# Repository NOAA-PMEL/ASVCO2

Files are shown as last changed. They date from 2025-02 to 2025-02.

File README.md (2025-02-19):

# ASVCO2
Open Source Repository for the Autonomous Surface Vehicle CO2 (ASVCO2) gen2 system's firmware and electronics hardware.

## Attribution
You agree to acknowledge NOAA-PMEL and UW on splash pages, and in publications, for products developed with this software.

## UW License
*Refer to the LICENSE file.*

## NOAA Legal Disclaimers
*NOAA does not intend to patent this work worldwide. It may be used freely, but NOAA does not warrant its fitness for any use.*

*As a work of the United States Government, the associated schematics and software are in the public domain within the United States. Additionally, NOAA waives any potential copyright and related rights in the associated schematics and software worldwide.*

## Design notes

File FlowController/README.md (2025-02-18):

# EDD-FlowController
Dedicated Flow Controller module which can control up to eight valves, four small motors, or a combination of both.  Design is originally for MApCO2 refresh project.

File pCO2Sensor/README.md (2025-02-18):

# EDD-pCO2Sensor
Gen2 pCO2 sensor based off of MApCO2 technology, upgraded with MSP430FR and active parts.

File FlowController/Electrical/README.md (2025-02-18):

# EDD-flow-controller-kicad
KiCad port of ASVCO2 Flow Control board

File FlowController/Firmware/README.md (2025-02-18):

# FlowController - Firmware
## Changelog
v1.2 SPON, SPOFF/SPVENT valve setting changed.  

## Build tools
This project uses the following build tools:
| Tool | Version | Description |
|----|----|----|
| IAR Embeddded Workbench for MPS430 | v7.20.1 | Embedded C/C++ Compiler for MSP430|
| Ceedling | 0.28.2 | Automated testing framework for C applications |
| CException | 1.3.1.18 | Simple Exception Handling for C|
| CMock | 2.4.4.215 | Mocking framework used with Ceedling |
| Unity | 2.4.1.120 | Unit test framemwork |

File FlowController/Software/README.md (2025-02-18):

# Flow Controller User Interface
## Overview
This document contains operational information for the Flow Controller Graphic User Interface, Command Line Interface and direct communication with the Flow Controller over RS-232

----------------------------------------------------------------
## Python Installation Instructions
The CLI and the GUI require Python 3.9 or later to be installed, as well as a virtual environment to run in.  
### Creating a virtual environment and installing required packages
1. Install Python 3.9 or later if not already installed
2. Open a terminal (In windows you can use CMD or PowerShell)
3. Navigate to this README directory (path/EDD-FlowController/Software/FlowControllerUI/)
4. run the following commands
    ```cmd
    > python -m venv .venv
    For Windows
    > .venv\Scripts\activate
    for Linux
    > source .venv/bin/activate
    
    > python -m pip install -r requirements.txt
    ```
5. Wait for the packages to be installed and then the GUI and CLI will be ready to run

----------------------------------------------------------------
## Direct Communication with Flow Controller (RS-232)
The Flow Controller uses a simple RS-232 interface to communicate with the host (ASVCO2, user, etc.).  

### RS-232 Settings
* Baudrate: 9600
* Bits: 8
* Flow Contro: None
* Stop Bits: 1

### RS-232 Commands
* All commands are terminated with "\r\n"
* All commands respond with ACK (0x06) if valid or NACK (0x15) if invalid
  * This response will be referred to as *\<A/N\>* in the following table
* All command respond with current 6 valve and 1 pump settings
    *  (ABABAB1 would be V1=ac, V2=bc, V3=ac, V4=bc, V5=ac, V6=bc, Pump=ON))
    *  This Response will be referred to as *\<VALVE\>* in the following table

| Command | Response | Description |
| --- | --- | --- |
| mode | *\<A/N\>* **MODE: XXX**\r\n *\<VALVE\\>* | Get the current mode |
| mode=SSSSS | *\<A/N\>* *\<VALVE\>* | Set the Mode to SSSSSS *See modes below | 
| vac=X | *\<A/N\>* *\<VALVE\>* | Set Valve X to position AC |
| vbc=X | *\<A/N\>* *\<VALVE\>* | Set Valve X to position BC |
| current | *\<A/N\>* **CURRENT: X**\r\n *\<VALVE\>* | Read Current Setting (1 - 7) |
| current=X | *\<A/N\>* *\<VALVE\>* | Set the Current Setting to X (integer)|
| pulse | *\<A/N\>* **PULSE: XXX**\r\n *\<VALVE\>*  | Read the Pulse Length in milliseconds (10-100) |
| pulse=XXX | *\<A/N\>* *\<VALVE\>* | Set the pulse length in milliseconds (integer 10 - 100) |
| ver | *\<A/N\>* **VERSION: vMM.mm-bb-hhhhhhhh**\r\n *\<VALVE\>* | Firmware Version |
| count | *\<A/N\>* **COUNT: XXX**\r\n *\<VALVE\>* | Read the Count (number or power cycles) |

| Mode Command | Description |
|---|---|
| ZPON | Zero, Pump ON |
| ZPOFF | Zero, Pump OFF |
| ZPPCAL | Zero, Post Cal |
| ZPVENT | Zero, Vent |
| SPON | Span, Pump ON |
| SPOFF | Span, Pump OFF |
| SPVENT | Span, Vent |
| SPPC | Span, Post Cal |
| EPON | Equilibrate, Pump ON |
| EPOFF | Equilibrate, Pump OFF |
| EPVENT | Equilibrate, Vent |
| EPPOST | Equilibrate, Post run |
| APON | Air, Pump ON |
| APOFF | Air, Pump OFF |
| APPOST | Air, Post run
| REST | Rest mode |
| DEPLOY | Deploy mode |
| PRES | Pressurize mode |
| PURGE | Purge mode |
| CLEAR | Clear mode |

----------------------------------------------------------------
## Command Line Interface (CLI)
Within this director is a python-based command line interface to interact with the Flow Controller
without needing to send direct commands over the RS-232 port.  

### Requirements
Follow the preceding Python Installation Instructions before running the CLI

### CLI Usage
Note: At any time within the terminal, you can use the tag ```--help``` to see a description of the commands

To initialize the CLI for the correct serial port, use the following instructions.  Once run, a .env file is 
generated and you will not need to run this command unless the serial port changes.
1. Open a terminal to the path specified in the Python Installation Instructions above
2. Find the serial port your Flow Controller is attached to and run the following command:
    * ```> python cli.py setup <PORT>```
    * ```<PORT>``` is the port number (COM12, /dev/ttyUSB0, etc.)

#### CLI Commands
To use the CLI, run the command ```> python cli.py COMMAND ARGS``` 

| Command (CMD) | Arguments (ARGS) | Description | Returns |
|--- | --- | --- | --- |
| info | (None) | Retreive information from the Flow Controller | ```FW Version: vX.Y-Z-hhhhhhhh``` <br> ```Pulse: XX``` <br> ```Current: X``` <br>```Count: XXX``` <br> ```Mode: XXXXXX``` |
| mode | None or \<Mode Command\> | If no argument, returns current mode setting.  If Mode Command sent, sets to specified mode and returns mode setting | ```Mode: XXXXXX``` |
| state | None | Retrieve the current valve state | ```Current State: VVVVVV``` |
| valve | Valve # (1-6), Direction (a or b) | Sets the specified valve to specified direction |  ```Current State: VVVVVV``` |
| valves | VVVVVV where V is A or B for valve position | Sets all the valves to the value requested | ```Current State: VVVVVV``` |

### Example Commands

| Command | Description |
| --- | --- |
| ```python cli.py mode EPON``` | Set the Flow Controller mode to Equilibrate, Pump ON |
| ```python cli.py valve 3 b``` | Set Valve 3 to position *bc* |
| ```python cli.py valves AAABBB``` | Set valves to ***V1=AC***, ***V2=AC***, ***V3=AC***, ***V4=BC***, ***V5=BC***,***V6=BC*** |
| ```python cli.py info``` | Returns the system information |
| ```python cli.py state``` | Returns the valve states |

----------------------------------------------------------------
## Graphic User Interface
The graphic user interface is designed to be the most intuitive interface for users not 
familiar with command line interfaces or direct RS-232 control.  

1. Open a terminal to the path specified in the Python Installation Instructions above
2. Run the following command:<br>
    ```> streamlit run .\gui.py```
3. Wait for the web page to load.

#### Connect to Device
* In the sidebar, select the serial port attached to the Flow Control board and press "Connect"
![First Steps](./FlowControlUI/img/DashboardStart.png)

### GUI Control
#### Updating System Information
* System Information can be changed using the fields in the sidebar.  Press "Update" when you want the changes to be saved to the device.
![System Info](./FlowControlUI/img/DashboardSystem.png)

#### Current Valve Positions
* The current valve state is shown in the "Current Valve Settings" section.  It is auto-updated after any control command is selected.
![Valve Setting](./FlowControlUI/img/DashboardState.png)

#### Set Individual Valve Position 
* To set individual valves, use the buttons in the "Individual Valve ControL" Section.  Vx:ac sets Valve "x" to 'ac' position, while Vx:bc sets valve "x" to 'bc' position.
![Single Valve](./FlowControlUI/img/DashboardValves.png)

#### Set Valves to Pre-programmed Mode
* To set the valves to the pre-programmed ASVCO2 positions, use the buttons in the "Set Mode" section.
![Valve Setting](./FlowControlUI/img/DashboardMode.png)

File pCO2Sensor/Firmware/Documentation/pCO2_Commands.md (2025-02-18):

# List of pCO2 Commands (Non-Console Command Set)

If a command is listed as **R/W**, send the command with a \<CR>\<LF> to read the value.  Add an \= to the command, plus the data to set in the format shown to write the value.

## System Setting Commands
The following system commands are also available:

| Command | Read/Write | Function |
|---|---|---|
| ? | R | Display list of commands | 
| ^C | W | (x3) Exit Logging by reset (kill process and reset system) |
| ver | R | Current software/firmware version |
| serial | **R/W** | Sensor serial number |
| system | R | Display all system settings |
| tasks | R | Display task information in scheduler |
| startup | R | Startup count |
| sreset | W | Software reset | 
| reset | W | Hardware reset |

### ? 
Displays list of PCO2 Commands available to user

### ^C
Control-C: Kills current process

### Q
Quit the console and return system to sleeep mode.

### ver 
Displays the current firmware version

### serial

Sensor serial number.  Has format:
~~~
serial= yyssss
~~~
yyssss is an 6-digit number.  Will be appended to "who" to form "pco2yyssss"
* yy is 2-digit year
* ssss is 4-digit serial number

### tasks? 
Current task queue information 

### system
Displays all the system settings

### startup 
Displays the number of system resets

### sreset
Reset the system by software (instant reset)

### reset
Reset the system by triggering watchdog (delayed).

**NOTE:** This only works if the watchdog bypass jumper has been removed.

## TELOS compliant commands
| Command | Read/Write | Function |
|---|---|---|
| cshow | **R** | Show Comm Data |
| gps | **R**  | GPS Data (always -2) |
| time | **R/W** | Sensor time |
| idata | **R** | Iridium Formatted Data |
| sdata | **R** | Sensor Raw Data |
| who | **R/W** | Serial number|

### cshow
Comm data.  Includes Com name, sensor name, sample start time, sample interval and sample period.
 Format as follows:

~~~
    COMM1
    PCO2
    samplestart = HH:MM:SS
    sampleinterval = HH:MM:SS
    sampleperiod = HH:MM:SS
    NA
    samplestart = 00:00:00
    sampleinterval = 00:00:00
    sampleperiod = 00:00:00
    NA
    samplestart = 00:00:00
    sampleinterval = 00:00:00
    sampleperiod = 00:00:00
~~~

* HH is two digit hour
* MM is two digit minute
* SS is two digit second

### gps
GPS data.  Always -2 for PCO2 sensor.
Return format as follows:
~~~
    gps= -2
~~~

### time
Time data.  Can be written or read.  
~~~
    time= yy mm dd HH MM SS
~~~
* yy is two digit year
* mm is two digit month
* dd is two digit date
* HH is two digit hour
* MM is two digit minute
* SS is two digit second

### idata
Iridium formatted data.  Has format:

/* @todo Add to this */

~~~
    %%HEADER
    DT,Mode,xxxxxxxx
~~~

### sdata
Sensor raw data.  Has format:
/* @todo Add to this */
~~~
    Header
~~~

### who
Sensor serial number.  Has format:

~~~
    who=SSSSYYNNNN
~~~

* SSSS Four char Sensor Name (pco2)
* YY Two-digit year
* NNNN Serial Number

## PCO2 Individual Configuration Commands
| Command | Read/Write | Function |
|---|---|---|
| span | **R/W** | Span Gas Concentration (ppm) |
| spandiff | **R/W** | Span Pressure Difference (kpa) |
| interval | **R/W** | Normal Mode Cycle Interval (hours) |
| change | **R/W** | Length of Fast Mode Sampling |
| equil | **R/W** | Length of equilibrator pump (seconds) |
| warmup | **R/W** | Length of LI8X0 Warmup (seconds) |
| pumpon | **R/W** | Length of pumping during a cycle (seconds) | 
| pumpoff | **R/W** | Length of pump off during a cycle (seconds) |
| sampleco2 | **R/W** | Length of data sampling during a cycle (seconds) |
| vent | **R/W** | Length of delay between opening and closing vent (seconds) |
| heater | **R/W** | Sets Licor Heater ON or OFF |
| sample | **R/W** | Data sampling interval (Hz) |

### span 

Sets the span gas concentration (in ppm).  
~~~
span= nnn.nn
~~~
* nnn.nn is floating point value for the attached span gas

### spandiff

Sets the span pressure difference (in kPa) for performing the span calibration.  

~~~
spandiff= p.pp
~~~

* Floating point value for the pressure difference.  Entering 0 sets sensor to always perform span cal.

### sample

Sample is the data sampling interval, in Hertz (1/s)

~~~
sample= n
~~~
* n is sample interval.  Acceptable values are 1, 2, or 4  (Hz)

### interval
Sets the normal mode cycle interval (hours).
~~~
interval= hh
~~~
* hh Hours between normal mode cycles

### change
Sets the fast mode cycle interval.
~~~
change= hh mm ss
~~~
All values are combined to produce total interval offset.

* hh Hours between cycles
* mm Minutes between cycles
* ss Seconds between cycles

### equil
Sets the length of equilibration pumping (seconds).
~~~
equil= sss
~~~
* sss Seconds of equilibration pumping

### warmup
Sets the length of Licor Li8x0 warmup before first cycle in sample
~~~
warmup= sss
~~~
* sss Seconds of Licor warmup

### pumpon
Sets the length of pumping during a cycle
~~~
pumpon= sss
~~~
* sss Seconds of Pump on 

### pumpoff
Sets the length of pumping off time before a sampe during a cycle
~~~
pumpoff= sss
~~~
* sss Seconds of Pump off

### sampleco2
Sets the length of time to sample over during a cycle
~~~
sampleco2= sss
~~~
* sss Seconds of sampling during a cycle

### vent
Sets the length of delay before closing the vent.  Applies to both vent 1 and 2
~~~
vent= sss
~~~
* sss Seconds of venting during a cycle

### heater
Sets the Licor heater on or off.
~~~
heater= n
~~~
* n State of Licor heater.  0 is OFF, 1 is ON

## Logging Commands
The following commands are used for setting the PCO2 sensor into its various logging modes.  This is a write-only function.

| Command | Function | Mode |
|---|---|---|
| log | Start logging | Fast Mode |
| fast | Start logging | Fast Mode |
| normal | Start logging | Normal Mode |
| norm | Start logging | Normal Mode |
| dep | Start deployment | Deployment Mode |
| depl | Start deployment | Deployment Mode |

### log *or* fast
Starts logging with fast mode.
~~~
log
fast
~~~

### normal *or* norm
Starts logging with normal mode.
~~~
normal
norm
~~~

### dep *or *depl*
Start deployment mode
~~~
depl
dep
~~~

### test
Set the system to TEST MODE, allowing access to test commands.
~~~
test
~~~   

## Valve Setting commands
These commands are for testing the sensor in different valve configurations.  Test mode is entered after this command.  All commands are write-only.

| Command | Function | 
|---|---|
| apos | Air position test loop |
| epos | Equilibrator position test loop |
| rpos | Rest position test loop |
| spos | Span position test loop |
| zpos | Zero position test loop |
| nopos | Start the test loop without changing valves |
| valves | Set valves to sequence selected (NOT CURRENTLY IMPLEMENTED) |
| valve | Set inidividual vale to selected (NOT CURRENTLY IMPLEMENTED) |

### apos
Sets the valves to the Air position.  Puts system in TEST MODE.
~~~
apos
~~~

### epos
Sets the valves to the Equilibrator position.  Puts system in TEST MODE.
~~~
apos
~~~

### rpos
Sets the valves to the Rest position.  Puts system in TEST MODE.
~~~
rpos
~~~

### spos
Sets the valves to the Span position.  Puts system in TEST MODE.
~~~
spos
~~~

### zpos
Sets the valves to the Zero position.  Puts system in TEST MODE.
~~~
zpos
~~~

### nopos 
Keeps valves in current positions.  Puts system in TEST MODE.
~~~
nopos
~~~

### valves

***NOT CURRENTLY IMPLEMENTED***

Set the valves to the sequence entered.

~~~
valves= x1 x2 x3 x4 x5 x6 p
~~~

* xy is the valve number and setting.
* x can be 'a' for flow 'CA' or 'b' for 'CB' (See valve flow diagrams)
* p is the Pump setting.  0 = OFF, 1 = ON

Example:
The following would set the condition for Zero with pump off, vent closed (POST CAL) 

~~~
valves= b b b b a b 0
~~~

The following would set the condition for Air Mode, pump ON

~~~
valves= a b b a a a 1
~~~

### valve

***NOT CURRENTLY IMPLEMENTED***

Set a single valve to the setting entered

~~~
valve= n x
~~~

* n is the valve number (1 - 6)
* x is the valve setting.  'a' for flow 'CA' or 'b' for 'CB' (See valve flow diagrams)

## Test Mode Command
This command puts the system in test mode.  Test mode supresses all scheduled runs 
until the system re-enters normal mode.  The following commands are write-only.

| Command | Function |
|---|---|
| test | Start the test loop without changing valves |

### test 
Enter Test Mode.  Allows for the remaining commands in this document to be run.
~~~
test
~~~

## Licor Commands 

| Command | Read/Write |Function | 
|---|---|---|
| licoron | R | Turn Licor ON |
| licoroff | R |Turn Licor OFF |
| licorcfg | R | Run Licor Configuration Sequence |
| lizero | R/W | Zero the Licor |
| lispan | R/W | Span the Licor (Span 1) |
| lispan2 | R/W | Span the Licor (Span 2) |
| lisample | R | Read the Licor Data |
| heaton | R/W | Turn the Licor Heater ON |
| heatoff | R/W | Turn the Licor Heater OFF |   
| lipass | W | Allow direct access to LICOR UART |

### licoron 
Turn Licor ON 
~~~
licoron
~~~

### licoroff
Turn Licor OFF 
~~~
licoroff
~~~

### licorcfg
Run licor configuration routine.
~~~
licorcfg
~~~

### lizero
Zero the Licor and return the coefficient.  Without the = returns the current coefficient without zeroing the system.
~~~
lizero= 
~~~

### lispan
Span the Licor and return the coefficient.  Withouth the = returnst he current coefficient withou spanning the system.
~~~
lispan= XXXX.XX
~~~

where 
XXXX.XX is the gas concentration of CO2 in PPM.

### lispan2
High span the Licor and return the coefficient.  Withouth the = returnst he current coefficient withou spanning the system.
~~~
lispan2= XXXX.XX
~~~

where 
XXXX.XX is the gas concentration of CO2 in PPM.

### lisample
Sample the Licor.  Returns data from Licor.
~~~
lisample
~~~

### heaton
Turn the Licor Heater ON.
~~~
heaton
~~~

### heatoff
Turn the Licor Heater OFF.
~~~
heatoff
~~~

### lipass
Allow direct access to Licor UART port.  This allows for communicating directly with the Licor.  This command turns the Licor power ON and starts the pass-through.  Send 3 consecutive Ctrl-C characters to restart the system in normal mode.

~~~
lipass
~~~

## Flow Control Commands 

| Command | Function |
|---|---|
| flowon | Turn Flow Control ON |
| flowoff | Turn Flow Control OFF |

### flowon
Turn Flow Controller Power ON.  Puts the valve block in DEPLOY with PUMP OFF.
~~~
flowon
~~~

### flowoff
Turn Flow Controller Power OFF 
~~~
flowoff
~~~

## Oxygen (O2) Sensor Commands 
| Command | Function |
|---|---|
| o2 | Read O2 Sensor |
| o2volt | Read O2 Port Voltage |
| o2int | Interval in days between O2 Calibration |
| o2time | Time of day for O2 calibration to occur |
| anaon | Analog Reference ON |
| anaoff | Analog Reference OFF |

### o2 
Read the O2 sensor and display the results.

~~~
o2
~~~

The response is in the format:

~~~
O2= yyy.yyy
~~~

* yyy.yyy is percent (%) O2

### o2volt
Read the O2 Sensor port voltage and display the results.

~~~
o2volt
~~~

The response is in the format:

~~~
o2volt= yyy.yyy
~~~

* yyy.yyy is the voltage in volts (DC).

### o2int
***NOT CURRENTLY IMPLEMENTED***

### o2time 
***NOT CURRENTLY IMPLEMENTED***

### anaon 
Turn the analog power port ON 

~~~
anaon
~~~

### anaoff
Turn the analog power port OFF
~~~
anaoff
~~~

### anapwron

***NOT CURRENTLY IMPLEMENTED***

Turn Analog Voltage Reference ON
~~~
anapwron
~~~

### anapwroff
***NOT CURRENTLY IMPLEMENTED***

Turn Analog Voltage Reference OFF
~~~
anapwroff
~~~

## Relative Humidity (RH) Sensor Commands
| Command | Function |
|---|---|
| rh | Read RH Sensor (RH + Temperature) |

### rh
Read the Relative Humidity sensor anre display the results.

~~~
rh
~~~

The response is in the format:

~~~
rh= yyy.yyy
temperature= zzz.zzzdegC
~~~

* yyy.yyy is the relative humidity in %RH
* zzz.zzz is the temperature in degrees C

## Real-Time Clock (RTC) Commands
| Command | Read/Write | Function |
|---|---|---|
| rtcon | R | Output RTC 32kHz signal |
| rtcoff | R | Supress RTC 32kHz signal |
| rtcset | R/W | Set RTC 32kHz Frequency |

### rtcon
***NOT CURRENTLY IMPLEMENTED***

### rtcoff
***NOT CURRENTLY IMPLEMENTED***

### rtcset
***NOT CURRENTLY IMPLEMENTED***

## LED Commands 
| Command | Function |
|---|---|
| grnon | Turn Green LED ON |
| grnoff | Turn Green LED OFF |
| redon | Turn Red LED ON |
| redoff | Turn Red LED OFF |

### grnon
Turn Green LED ON 
~~~
grnon
~~~

### grnoff
Turn Green LED ON 
~~~
grnoff
~~~

### redon
Turn Red LED ON 
~~~
redon
~~~

### redoff
Turn Red LED OFF
~~~
redoff
~~~

### spareon
Turn Spare Power ON 
~~~
spareon
~~~

### spareoff
Turn Spare Power OFF
~~~
spareoff
~~~

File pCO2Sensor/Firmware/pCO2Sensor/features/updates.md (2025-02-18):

# List of feature additions

## v1.9.4
### Issue 141
* Fixing Data headers from:
  * ***WAS:*** State,TS,CO2(ppm),Li_Temp(C),Li_Pres(kPa),Li_Raw,Li_Ref,RH(%),RH_T(C),O2(%),xCO2(dry),xCO2_(wet), co2kzero, co2kspan, co2kspan2, errors
  * ***NOW IS:*** State,TS,CO2(ppm),Li_Temp(C),Li_Pres(kPa),Li_Raw,Li_Ref,RH(%),RH_T(C),O2(%),SW_xCO2_(dry),Atm_xCO2(dry) , co2kzero, co2kspan, co2kspan2, errors

## v1.9.5
### Issue 145
* Increase timeout time on Command port
  * Timeout is now 60 seconds (was previously 10 seconds)

## v1.9.7
### Issue 148
* Remove ssconc as settable variable
  * ssconc is another variable id for span2, but is not settable
  * User settable has been removed for ssconc. 
  * span2 still works.

## v1.9.9
### Issue 149
* Spandiff error in firmware v1.9.1
  * Ran through multiple tests with no spandiff (spandiff=0.1, actual diff=0.0035)
    * No error found
  * Manually set atmospheric to 101.7kPa
    * Still no error
  * May have been fixed in v1.9.3 although no code showing changes at that point

## v1.9.11
### Issue 155
* Change span concentration to 300ppm default
  * default was 500ppm
  * now is 300ppm

## v1.9.13
### Issue 166
* Adding Flow Control pass-through mode.
  * in ***TEST*** mode, use the command ```flowpass``` to enter flow passthrough mode.
  * pCO2 now acts like a bidirectional passthrough for the flow control module.

## v1.9.14
### Issue 166
* Improving flow control pass-through.
  * ASCII ACK(0x06)/NAK(0x15) is interpreted and written as a string
  * Removal of characters under (0x20) except for ACK, NAK, CR and LF
  * More consistent pass-through experience.

## v1.10.0
Updates completed during M.C. contract through 7/22

[v1.9 Milestones to reach 1.10](https://github.com/NOAA-PMEL/EDD-pCO2Sensor/milestone/6)

* Main Control board Improved error handling conditions
* Flow control board improved error handling conditions
* Self-recovery and error logging of reset types
* SData improved sampling to capture 60 samples (also with normal logging)
* SPON flow time is now it's own setting
* Span, Span2 coefficient resilience
* Valve pulse time now settable from main controller
* Valve current setting now settable from main controller
* idata and sdata headings changed.  
* span gas default is now 300ppm
* ssconc is now read-only
* command timeout length increased from 10sec to 60sec
* tsq now recovers write after completion/reset

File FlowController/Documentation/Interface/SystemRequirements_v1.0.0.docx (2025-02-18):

# Electrical/Firmware requirements specification

for

MApC02 Gen2

Version 0.1

Prepared by Matt Casari

PMEL/EDD

August 2, 2017

REVISION HISTORY

NAME | DATE | CHANGES | VERSION
M.Casari | 8/2/2017 | Initial Release | 0.1

# 1 Introduction

## 1.1 Purpose

The purpose of this document is to present an electrical & firmware systems overview for the proposed second generation Moored Autonomous Partial Pressure Carbon Dioxide (MApCO2) sensor. This document covers all requirements for essential functionality of the new sensor to preserve, at minimum, the functionality of the first generation MApCO2 sensor.

## 1.2 Document Conventions

### 1.2.1 Essential Definitions, Acronyms and Abbreviations

The following definitions, acronyms and abbreviations are considered important to the general reading of this document. A more comprehensive list of terms can be found in Appendix A: Glossary.

Table 1. Definition of important terminology.

Term | Definition
NOAA | National Oceanic and Atmospheric Administration
PMEL | Pacific Marine Environmental Laboratory
DOC | Department of Commerce
MApCO2 | Moored Autonomous Partial Pressure Carbon Dioxide
GUI | Graphical User Interface
User | System or subsystem user, could be human or machine
Firmware | Embedded system (microcontroller) code
i-Data | Iridium Formatted Data (PMEL Format)
s-Data | Standard Formatted Data (PMEL Format)

Table 2. Requirements terminology.

Term | Definition
SHALL | Hard Requirement, considered critical to functionality of the system/project.
WILL | Intermediate requirement, to be implemented if time permits.
SHOULD | Lowest priority. Concept is not complete at the time of writing this document and further investigation may determine this feature is unnecessary.

## 1.3 Intended Audience and Reading Suggestions

- System developers, such as engineers, technicians, scientists and administrators.
- Typical Users, such as scientists, engineers and technicians in the NOAA PMEL organization.
- External users, such as scientists and engineers in partnering institutions or industry.
- Programmers and data analysts who will interface with the system remotely.

## 1.4 Project Scope

The second generation of MApCO2 sensors (MApCO2Gen2) is an electrical hardware and firmware upgrade to the first generation of pCO2 sensors. This document will cover both hardware and software requirements for the system, as well as practices to be used during development.

This document will not cover the specific interface specification to communicate with the system. See the TBD for more information regarding communications. At minimum, the system shall have the basic functionality of the Battelle Interface Specification [4].

## 1.5 References

### 1.5.1 Documentation References

[1] Musielewicz,S. (2015). MApCO2 User Manual, NOAA/PMEL, Settle, WA
[2] Battelle. (2009). System Manual for Seaology pCO2 Monitor, Battelle, Columbus, OH.
[3] Battelle. (2010). User Manual for the pCO2 System Software Version 03.18, Battlelle, Columbus, OH.
[4] Battelle. (2009). Interface Specification for the pCO2 Sensor System, Battelle, Columbus, OH.
[5] “Battelle Seaology® pCO2 Monitoring System.” pCO2 Monitoring System, Battelle, www.battelle.org/government-offerings/national-security/maritime-systems-technologies/sensors/pco2-monitoring-system.
[6] Preston-Werner, Tom. “Semantic Versioning 2.0.0.” Semantic Versioning, Github, semver.org/
[7] Patel, Amit, et al. “Google Python Style Guide.” Google Python Style Guide, Google, google.github.io/styleguide/pyguide.html.

### 1.5.2 Project Websites

The project repository for this development can be found at https://github.com/NOAA-PMEL/EDD-MApCO2.

# 2 Product description

## 2.1 Product Perspective

The system being developed is the second generation of moored autonomous partial carbon dioxide (MApCO2Gen2) system, focusing on the upgrade and replacement of obsolete electronics found in the first generation systems. The new system will utilize all existing housings and sensors used by the previous system, allowing for a drop in replacement as the older system electronics degrade over time. The new system will follow a modular design paradigm, allowing for quick replacement of individual sensors as well as provide integration of newer sensors without major revisions to the systems firmware. The system has capabilities for measuring pCO2 from seawater and air using a custom designed flow system and a LiCor 820/840. Interfaces for CTD, Oxygen optode and pH sensors will be available. User will have a graphical user interface to program sampling schedules. Data measurements will be stored internally while statistical sampling will be transmitted via Iridium or cellular modem.

## 2.2 Product Functions

The MApCO2Gen2 has the following functions:

- Collect, dry and measuring surface air samples; measure pCO2 concentrations.
- Collect and process (sea)water samples; measure pCO2 concentrations.
- Measure (sea)water conductivity and temperature.
- Measure (sea)water pH via external sensor.
- Measure dissolved oxygen in (sea)water.
- Perform sampling of sensors and control of flow systems on a user defined schedule.
- Record sensor and system data on removable storage drive.
- Connect and save data subsets to user network storage via Iridium or cellular modem.

The configuration GUI shall have the following functions:

- Master controller scheduling configuration.
- Subsystem parameters, configurations and settings interface.
- Monitor and display data from sensors and systems in real-time for bench testing.

## 2.3 User Classes and Characteristics

<Identify the various user classes that you anticipate will use this product. User classes may be differentiated based on frequency of use, subset of product functions used, technical expertise, security or privilege levels, educational level, or experience. Describe the pertinent characteristics of each user class. Certain requirements may pertain only to certain user classes. Distinguish the most important user classes for this product from those who are less important to satisfy.>

## 2.4 Operating Environment

The MApCO2Gen2 system shall be built on custom printed circuit boards (PCBs) with custom firmware. Where possible, the subsystems shall reuse code from other subsystems to provide a consistent code base. A real-time operating system (RTOS) may be used if it meets the timing and performance requirements discussed in this document. Preference shall be given to an open-source RTOS and other tools.

The GUI system shall be developed on the Windows operating system. Where possible, the code should be written to be useable cross-platform. The GUI source code shall be open to other users who wish to port it to other operating systems.

## 2.5 Design and Implementation Constraints

### 2.5.1 Functional Requirements

#### 2.5.1.1 Basic Requirements to Meet Generic Specifications

The MApCO2Gen2 system shall meet the following minimum general functional requirements of the first generation MApCO2 system (modified from system performance specification on the Battelle pCO2 webpage [5]):

1. Provide time series measurements of ocean carbon and air sea exchange to monitor carbon cycle variability.
2. Feature a measurement range of 100 to 600 ppm or greater (with an extended range available) and a precision of about 1ppm.
3. Offer ease of operation, set up and deployment.
4. Functions continuously for more than one year without intervention.
5. Feature two-way satellite data transmission capabilities that control the system and receive data in near real-time.

#### 2.5.1.2 System Performance Requirements

The system shall conform to the following minimum requirements

1. The system shall be capable of measuring a pCO2 range between 100 and 600 ppm.
2. The system shall have a precision of approximately 1 ppm
3. The system shall have a maximum average current draw of 24mA over 24 hour (not including Iridium/Communications).
4. Iridium/Communications shall have a maximum average current draw of 3mA over 24 hours.
5. The system shall have a means of (limited) two-way communication over Iridium or other wireless communication systems.
6. The system shall be easy to operate, set up and deploy.
7. The system communications interface shall be backwards compatible with the first generation MApCO2 system.
8. The new system shall be designed to fit into all first generation housings.
9. The new system shall utilize the same connector and external wiring as the first generation system.

### 2.5.2 Hardware requirements

#### 2.5.2.1 Memory Constraints

- There is no specified memory constraints for the embedded system, provided that all tasks and schedules can be fulfilled to their minimum requirements.
- For the GUI and other desktop/laptop programs used to interface to the embedded system shall have a minimum memory requirement of TBD.

#### 2.5.2.2 Timing Requirements

- All measurements on the CO2 embedded system happen at a 1Hz rate maximum. The firmware shall be designed to sample/operate at 10Hz or better to capture any future use cases for the system.
- For the desktop/laptop programs, any modern computer (circa 2010 and newer) shall be sufficient.

#### 2.5.2.3 Communication

- The user shall have the ability to connect to the system via RS-232 or USB virtual COM port communications.
- The system shall be capable of serial communications at baud rates of 9600 to 115200 (Standard baud rates only)

### 2.5.3 Specific Technologies and Tools

- A list of tools and associated software versions shall be maintained in a README file located in the main directory of the system project repository.

#### 2.5.3.1 EMBEDDED SYSTEM TOOLS

- For all embedded (sub)systems, Texas Instruments MSP430 or ARM Cortex-M microcontrollers shall be used.
- Any MSP430 microcontroller used shall be chosen from the MSP430FR family (ferromagnetic RAM) for their extreme low-power capabilities and extreme lifetime during multiple read/write cycles.
- For MSP430 devices, the IAR Embedded Workbench for MSP430 v7.10 and associated compiler shall be used.
- For ARM Cortex-M devices (if used), the IAR Embedded Workbench for ARM v8.11 and associated compiler shall be used.
- For embedded unit testing, Unity, Ceedling and CMock shall be used.

#### 2.5.3.2 SCHEMATICS AND PRINTED CIRCUIT BOARD DESIGN TOOLS

- PMEL uses Capilano Systems DesignWorks tool for schematic capture.
- MentorGraphics PADS is used for PCB layout design.
- Other tools may be used if they are compatible with either of the tools previously mentioned.

#### 2.5.3.3 SCRIPTING AND GRAPHICAL USER INTERFACE TOOLS

- Python shall be used as the primary language for any scripting. Python 3.6 or later shall be used.
- Any Graphical User Interface shall utilize open-source technologies; specifically Python, PyQt5, pyqtgraph and PySerial.

### 2.5.4 Language Requirements

- All embedded firmware shall be written in the C language, Assembly language (specific to the microcontroller) or a combination of both.
- GUI’s shall be written in Python using PyQt5 unless higher performance is determined necessary. C++ and Qt5 will be used for higher performance for those cases.

### 2.5.5 Security considerations

- NOAA and DOC security requirements shall be adhered to. Passwords, personally identifiable information (PII) or any other sensitive information SHALL NOT be included in any external documentation, files, repositories, etc.
- Any security techniques used in the development of the system shall be documented but not disseminated outside of PMEL without authorization from PMEL EDD.

### 2.5.6 Design Conventions

- The embedded source code shall be written to the ISO/IEC 9899:1999 (C99) standard. This requirement should be enforced by utilizing a lint program to identify adherence violations prior to a version release.
- Embedded systems should conform to the MISRA-C standard (MISRA-C 2004)
- All firmware source code shall use embedded commenting in the Doxygen convention so that Application Program Interface (API) documentation can be easily generated using the Doxygen tool.
- All Python scripts shall conform to the Google Python Style

## 2.6 User Documentation

### 2.6.1 Basic Documentation

Documentation delivered with this project will include:

- System User Manual
- System Wiring Diagrams
- System Bill of Materials
- System Communication Protocol
- Subsystem Schematics
- Subsystem Printed Circuit Board Gerber files
- Subsystem Bill of Materials
- Subsystem Datasheets
- Firmware reference documentation

### 2.6.2 Product repository

In addition to the aforementioned documentation, an online repository will be kept to provide a central location for development and dissemination of information. Github is currently used by PMEL EDD, and will be used for this system development. Only PMEL EDD personnel and those granted authorization by PMEL EDD will have access to the repository. See 6.1 for more detail regarding Revision Control.

At the time of project completion this repository shall contain the following file structure with all documents included and completed (Bold indicates folder, italic indicates file):

- Documentation
  - Readme
  - System User Manual
  - System Interface Communication Document
  - Subsystem A
    - User Guide
    - Communication Protocol
    - Calibration Instructions
    - Calibration Checklist
- Electrical
  - Readme
  - System Wiring Diagram
  - System Bill of Material
  - Subsystem A
    - Schematic
    - PCB Gerbers
    - Bill of Materials
    - Datasheets
  - Subsystem N …
- Firmware
  - Binaries
    - Binary Files
    - How-to (install) readme
  - Source Code
    - All Source Code Files
  - Test
    - Readme
    - Embedded Test
      - Firmware Test Files
    - System Test
      - System Test Files
  - Documentation
    - Embedded API Documentation
- GUI
  - Readme
  - Source Code
    - Source Code File
  - Test
    - Readme
    - Test Files
- Mechanical
  - Readme
  - Mechanical Drawings
  - Bill of Materials
  - Solid models TBD

## 2.7 Assumptions and Dependencies

It is assumed that the end-user or manufacturer of these system will have access to all tools required to flash (install) the binary code onto all microcontrollers in the system. Similarly, the user must have access to a computer with a USB port that can run the GUI.

Although it will be possible to configure the MApCO2 to accept new sensors, it is assumed that users outside of PMEL EDD shall work with PMEL EDD engineers to do so.

# 3 External interface Requirements

## 3.1 User Interfaces

A graphical user interface (GUI) shall be provided with the final delivered system. The GUI shall be able to connect to the system hardware via a serial (RS-232, RS-485, etc.) interface in an intuitive manner. If possible, the GUI shall have an “auto-connect” feature which scans all active COM ports on the GUI computer for the MApCO2 system.

The GUI shall provide an easy-to-use method of updating system parameters and settings to the user’s requirements. An import menu shall be available to load previous system configurations. Similarly, and export menu shall be available to save current configurations.

The GUI configuration shall have a simple method of adding/removing sensors from the current system. If possible, this shall be accomplished by a graphical means. At minimum, there shall be a drop-down menu based on known sensors to choose from.

The GUI shall include a data visualization function which can plot data in real-time or in bursts (typical Iridium transmit mode). The data visualization shall have the ability to plot multiple data streams simultaneously. There shall be a method to differentiate data streams by selecting color or other unique identifier for each plot.

The GUI shall have the option to log all data received from the system. The GUI default shall be to log all data to a file. The user shall have the option to rename the log file.

The GUI shall be able to auto-configure its basic layout/configuration based on the firmware version provided by the hardware system.

Keyboard shortcuts shall be identified in the drop-down menus by underlining the special keys to access the shortcut.

## 3.2 Hardware Interfaces

The system shall have the option to connect to the software console either via a RS-232 connection (3-wire Rx, Tx, GND) external to the enclosure (bulkhead connector) or a USB-to-serial “Virtual COM” port. These serial ports shall be capable of data transfer from 4800 to 115,200 baud, at typical baud rates.

The first revision hardware interface between the master controller and the subsystem controllers shall be a RS-232 or UART connections on a serial multiplexor or serial bridge. Alternatively, a RS-485 multi-drop system could be utilized if it was demonstrated that there would be no collisions or catastrophic failure should one subsystem fail. Subsequent hardware revisions should attempt to move toa system bus architecture to communicate commands and data.

The interface between master controllers or subsystem and any sensor or subsystem external to the housing should be electrically isolated, if possible

All hardware interfaces between low power electronics and electromechanical systems (solenoids, motors, etc.) should be electrically isolated, if possible.

## 3.3 Software Interfaces

< Describe the connection between this product and other specific software components (name and version), including databases, operating systems, tools, libraries, and integrated commercial components. Identify the data items or messages coming into the system and going out and describe the purpose of each. Describe the services needed and the nature of communications. Refer to documents that describe detailed application programming interface protocols. Identify data that will be shard across software components. If the data sharing mechanism must be implement in a specific way (for example, use of a global data area in multitasking operating system), specify this as an implementation constraint>.

## 3.4 Communications Interfaces

<Describe the requirements associated with any communications functions required by this product, including e-mail, web browser, network server communications protocol, electronics forms, and so on. Define any pertinent message formatting. Identify any communication standards that will be used, such as FTP or HTTP. Specify any communication security or encryption issues, data transfer rates, and synchronization mechanisms.>

The MApCO2 system must be capable of two separate communications paradigms; “Connected” and “Deployed”.

### 3.4.1 Connected Communications

“Connected” communications refers to all communications with the MApCO2 system while the system is tethered directly to the user (computer, etc.). In this mode, RS-232 communications shall be employed with a custom communication protocol, described a TBD interface control document, and backwards compatible with the previous Battelle Interface Specification [4].

### 3.4.2 Deployed Communications

“Deployed” communications refers to all communications that occur while the system is untethered and communicating via Iridium modem, Cellular modem, or other techniques. This mode shall adhere to the communication protocol described in the TBD interface control document in addition to the Battelle Interface Specification [4].

# 4 System Features

This section documents all of the system and subsystem features of the MApCO2Gen2 system, their requirements and optional features.

Requirements are considered essential.
Options are considered “nice-to-have” but will only be implemented if time permits.
Priorities are scaled between a low of 1 and a high of 9.

## 4.1 Main Control System (MCS)

### 4.1.1 Description and Priority

The MCS provides all communication and scheduling between subsystems (individual sensors and flow control systems) and the data storage system. Additionally, the MCS routes all data to/from the communications control system.

### 4.1.2 Stimulus/Response Sequences

The MCS shall have the following stimulus/response sequences:

1. MCS Power up shall provide indication of a stable ready state.
2. MCS system parameters shall be available at user request.
3. MCS status parameters shall be available at the user request.
4. MCS failures and error log shall be available at the user request.
5. MCS system options shall be available at the user request.
6. MCS shall have “pass-through” mode to allow user to directly communicate with sub-systems.
7. MCS shall have a system reset state which puts all sub-systems in the lowest, stable, power state.
8. MCS shall have features to set the system time for itself and all sub-systems.

### 4.1.3 Functional Requirements

REQUIREMENTS:

MCS-REQ-1: The console/user interface protocol shall be backwards compatible with the first generation pCO2 system. Priority = 9
MCS-REQ-2: The MCS shall use a microcontroller commonly used by PMEL OR a microcontroller with an architecture expected to remain non-obsolete for 10 (ten) years. Priority = 5
MCS-REQ-3: The MCS shall manage scheduling for all subsystems. Where scheduling can be offloaded to a specific subsystem (i.e. subsystems with RTC), the MCS MUST ensure time synchronization at intervals of six (6) hours or better. Priority = 9
MCS-REQ-4: The MCS shall include a unique ID chip which provides a unique 16-bit (or better) serial number.

OPTIONS:

MCS-OPT-1: The console/user interface should have the option of connecting to the user over a serial port OR USB port.
MCS-OPT-2: The MCS should be designed for the ability to move to a communication bus such as Controller Area Network bus (CANbus) or Local Interconnect Network (LIN) as a replacement for point-to-point serial (RS-232 or TTL) connections.
MCS-OPT-3: If the MCS implements CANbus for intercommunication, NMEA2000 should be considered as a high-level communications protocol.

## 4.2 Flow Control System (FCS)

### 4.2.1 Description and Priority

The FCS provides the system the ability to switch between CO2 purge mode, span gas mode, air CO2 measurement mode and ocean CO2 measurement mode. It handles all switching of solenoid valves, motor control and any feedback of those electromechanical devices.

### 4.2.2 Stimulus/Response Sequences

The FCS shall have the following stimulus/response sequences:

1. FCS Power up shall provide indication of a stable ready state.
2. FCS system parameters shall be available at user request.
3. FCS status parameters shall be available at the user request.
4. FCS failures and error log shall be available at the user request.
5. FCS system options shall be available at the user request.
6. FCS shall have user ability to control all valves either individually or as a group.
7. FCS shall have user pump control ability.
8. FCS should have predefined routines and schedules which can be called by the user.

### 4.2.3 Functional Requirements

REQUIREMENTS:

FCS-REQ-1: The FCS shall use latching valves which are capable of operating in low (TBD) temperatures. Priority = 9
FCS-REQ-2: The FCS shall be capable of driving the six (6) latching valves at the required voltage and current for a duration that is at least 500% over the typical duration required to switch the valves (time TBD). Priority = 9
FCS-REQ-3: The FCS shall be capable of driving a TBD pump at the required voltage and current for a duration TBD. Priority = 9
FCS-REQ-4: The FCS shall have protective fuses on the input to the drive electronics to prevent any
FCS-REQ-5: The FCS shall monitor the state of the input drive fuses to alert the user to any failure conditions. Priority = 7
FCS-REQ-6: The FCS shall have an onboard real-time clock (RTC) to run configurable profiles in sync with the main control system. Priority = 8
FCS-REQ-7: The FCB shall be capable of accepting battery voltages between TBD and providing voltage regulation to the valve and pump, if needed.
FCS-REQ-8: The FCB shall utilize electrical isolation between the driver circuitry and the logic control subsystems. Priority = 8

OPTIONS:

FCS-OPT-1: The FCS should be capable of monitoring the current profile the pump while energized.
FCS-OPT-2: The FCS should be capable of monitoring the current state of each individual valve.
FCS-OPT-3: The FCS should monitor the temperature of the valve block and provide an extended energized period during colder temperatures.
FCS-OPT-4: The FCS should be capable of monitoring the flow rate of the pumped fluid.

## 4.3 Communications Control System (CCS)

### 4.3.1 Description and Priority

The communication control system is responsible for all rou

### 4.3.2 Stimulus/Response Sequences

The CCS shall have the following stimulus/response sequences:

1. CCS Power up shall provide indication of a stable ready state.
2. CCS system parameters shall be available at user request.
3. CCS status parameters shall be available at the user request.
4. CCS failures and error log shall be available at the user request.
5. CCS system options shall be available at the user request.
6. CCS shall provide the GPS location at the users request.
7. CCS shall provide the Iridium signal strength at the users request.
8. CCS shall provide the ability to test Iridium communications at the users request.

### 4.3.3 Functional Requirements

SSS-REQ-1: The CCS shall have a command interface which is backwards compatible with pCO2g1. Priority = 9
SSS-REQ-2: The CCS shall be capable of communications of the IRIDIUM network. Priority = 9
SSS-REQ-3: The CCS shall be capable of providing GPS locations at regular intervals (TBD). Priority = 9
SSS-REQ-4: The CCS shall be capable of providing GPS fix when externally requested. Priority = 9
SSS-REQ-5: The CCS shall return zeros when the GPS fails to fix (or NaN). Priority = 5
SSS-REQ-6: The CCS shall have two configurable sampling modes, at minimum; Report every sample or Report every day. Priority = 8

OPTIONS

CCS-OPT-1: The CCS should be designed to communicate over IRIDIUM or Cellular Modems.

## 4.4 Serial Sensor Subsystem (SSS)

### 4.4.1 Description

The SSS is a module which commands and interprets sensors with serial communications. The SSS can interpret commands from the user (MCS or other), and based on configuration flies, provide data from one of the many sensors the MApCO2 system monitors. The SSS converts the native data format of the sensor into a PMEL format (e.g., i-Data, s-Data, etc.) before returning the data to the user.

### 4.4.2 Stimulus/Response Sequences

The SSS shall have the following stimulus/response sequences:

1. SSS Power up shall provide indication of a stable ready state.
2. SSS system parameters shall be available at user request.
3. SSS status parameters shall be available at the user request.
4. SSS failures and error log shall be available at the user request.
5. SSS system options shall be available at the user request.
6. SSS shall provide a sensor “pass-throught” mode at the user request.
7. SSS shall provide the i- and s-Data at the user request.

### 4.4.3 Functional Requirements

SSS-REQ-1: The SSS shall be capable of interfacing with serial (RS-232, RS-485, TTL) sensors at typical baud rates. Priority = 9
SSS-REQ-2: The SSS shall be capable of communicating with the following devices (AT MINIMUM):
  - LI-COR 820: All versions
  - Seabird SBE16: All versions
  - Seabird SeaFET: All versions
  - Sunburst Sensors SAMI2
  - Honeywell Durafet: All versions
  - Aanderaa 4831 Oxygen Optode
  - Aanderaa 4330 Oxygen Optode

OPTIONS:

SSS-OPT-1. Change the sys in the bullet list to reflect the acronym of abbreviated name of the system feature.

## 4.5 Data Storage System (DSS)

### 4.5.1 Description

The DSS provides all data storage for the MApCO2 system. This critical system provides the storage of all raw data from each of the sensors which the MCC controls.

### 4.5.2 Stimulus/Response Sequences

The DSS shall have the following stimulus/response sequences:

1. DSS Power up shall provide indication of a stable ready state.
2. DSS system parameters shall be available at user request.
3. DSS status parameters shall be available at the user request.
4. DSS failures and error log shall be available at the user request.
5. DSS system options shall be available at the user request.
6. DSS Save Data mode shall be available at user request.
7. DSS Retrieve Data mode shall be available at the user request.
8. DSS disk space shall be available at the user request.

### 4.5.3 Functional Requirements

REQUIREMENTS:

DSS-REQ-1: The DSS shall be able to record the data from each subsystem at size of up to 1MB per record. Priority = 4
DSS-REQ-2: The DSS shall save data in a format consistent with:
- Folder with the NAME of the sensor
- File name with the date of the data collection plus the serial number of the sensor
  - e.g. LICOR_381210
- Data will be timestamped according to when it was sampled
DSS-REQ-3: The DSS shall be able to interface over a serial connection at typical baud rates up to 115,200 baud. Priority = 5
DSS-REQ-4: The DSS shall use microSD cards as storage media. Priority = 6
DSS-REQ-5: The DSS shall be capable of using microSD cards exceeding 32GB in size, therefore requiring exFAT formatting. Priority = 7

OPTIONS:

DSS-OPT-1: The DSS should have redundancy when integrated into the MCS.

## 4.6 Battery Management System (BMS)

### 4.6.1 Description and Priority

The BMS is a dedicated system to monitor the battery packs in the MApCO2Gen2 system. At minimum, it will monitor the state of each pack and switch off packs.

### 4.6.2 Stimulus/Response Sequences

1. BMS Power up shall provide indication of a stable ready state.
2. BMS system parameters shall be available at user request.
3. BMS status parameters shall be available at the user request.
4. BMS failures and error log shall be available at the user request.
5. BMS should provide the current state of the battery pack(s) at the user request.
6. BMS should be able to switch battery pack on and off at the user request.
7. BMS should provide indication of fuse state at the user request.

### 4.6.3 Functional Requirements

REQUIREMENTS:

BMS-REQ-1: The BMS shall have the ability to monitor both battery packs to determine the current charge level. Priority = 9
BMS-REQ-2: The BMS shall provide fusing to prevent any short circuits from occurring. Priority = 7
BMS-REQ-3: The BMS shall be capable of switching battery connections to open if measurements indicate a failing or failed battery pack. Priorty = 1
BMS-REQ-4: The BMS shall be capable of switching battery connections by a user command (including commands by the control system). Priority = 9

OPTIONS:

BMS-OPT-1: The BMS should be designed for forward compatibility by offloading battery monitoring by type (e.g., Lithium, Alkaline, etc.) onto a dedicated module. Ability to monitor/manage ALL battery types is preferred, but not required.
BMS-OPT-2: The BMS should be designed for the ability to integrate energy harvesting techniques (e.g. Solar) in future revisions.
BMS-OPT-3: The BMS should monitor power statistics (i.e. average current, peak current, etc.) if it will not significantly affect battery life (power draw less than TBD).

## 4.7 Graphical User Interface (GUI)

### 4.7.1 Description and Priority

The Graphical User Interface shall be the primary tool used by system operators to connect to and configure the MApCO2 system. It

### 4.7.2 Stimulus/Response Sequences

1. The GUI shall auto-connect with the system at the user request.
2. The GUI shall configure the system at the user request.
3. The GUI should auto-generate or retrieve a unique serial number at the user request.

### 4.7.3 Functional Requirements

REQUIREMENTS:

GUI-REQ-1: The GUI shall be easy-to-use and have intuitive functions.
GUI-REQ-2: The GUI shall have a help menu.
GUI-REQ-3: The GUI shall have an import menu which retrieves previously saved configurations.
GUI-REQ-4: The GUI shall have an export menu to save the current configuration.
GUI-REQ-5: The GUI shall have the ability to plot pCO2 data.
GUI-REQ-6: The GUI shall graphically identify the current system state.
GUI-REQ-7: The GUI shall have a system auto-connect feature.

OPTIONS:

GUI-OPT-1: The GUI should have the ability to link all current configurations to a database.
GUI-OPT-2: The GUI should have the ability to control each sub-system individually.

## 4.8 System Feature 1

<Don’t really say “System Feature 1.” State the feature name in just a a few words.>

### 4.8.1 Description and Priority

<Provide a short description of the feature and indicate whether it is of High, Medium, or Low priority. You could also include specific priority component ratings, such as benefit, penalty, cost, and risk (each rated on a relative scale from a low of 1 to a high of 9).>

### 4.8.2 Stimulus/Response Sequences

<List the sequences of user actions and system responses that stimulate the behavior defined for this feature. These will correspond to the dialog elements associated with use cases.>

### 4.8.3 Functional Requirements

<Itemize the detailed functional requirements associated with this feature. These are the software capabilities that must be present in order for the user to carry out the services provided by the feature, or to execute the use case. Include how the product should respond to the anticipated error conditions or invalid inputs. Requirements should be concise, complete, unambiguous, verifiable, and necessary. Use “TBD” as a placeholder to indicate when necessary information is not yet available.>

<Each requirement should be uniquely identified with a sequence number or a meaningful tag of some kind.>

REQUIREMENTS:

SYS-REQ-1. Change the sys in the bullet list to reflect the acronym of abbreviated name of the system feature.

OPTIONS:

SSS-OPT-3. Change the sys in the bullet list to reflect the acronym of abbreviated name of the system feature.

# 5 Other NonFunctional Requirements

## 5.1 Performance Requirements

< If there are performance requirements for the product under various circumstances, state them here and explain their rationale, to help the developers understand the intent and make suitable design choices. Specify timing relationships for real-time systems. Make such requirements as specific as possible. You may need to state performance requirements for individual functional requirements or features.>

## 5.2 Safety Requirements

The design of the system shall adhere to all safety regulations enforced by NOAA and the DOC.

## 5.3 Security Requirements

Any documentation, source code, or other files which could be exposed to the public (i.e. stored on cloud services) shall not contain:

- Passwords
- Personally identifiable information (PII)
- Sensitive information as regulated by DOC and NOAA regulations

## 5.4 Software Quality Attributes

<Specify any additional quality characteristics for the product that will be important to either the customers or the developers. Some to consider are: adaptability, availability, correctness, flexibility, interoperability, maintainability, portability, reliability, reusability, robustness, testability, and usability. Write these to be specific, quantitative, and verifiable when possible. At the least, clarify the relative preferences for various attributes, such as ease of use over ease of learning.>

# 6 Other Requirements

## 6.1 Revision Control System

This project shall maintain revision control using Git, with the primary repository located on Github. All active developer participants in the project shall have administrative rights. Occasional contributors shall have read/write permissions. All other users shall have read permissions only. Access to a higher permission level shall be granted on an as-needed basis.

Active developers shall commit to the Github repository on a basis TBD by the project manager. Merge conflicts that cannot be easily resolved shall involve the project manager before committing to the project repository.

## 6.2 Version Numbers

Code versioning shall follow the rules of the Semantic Versioning 2.0.0 [5], as restated below:

Given a version number MAJOR.MINOR.PATCH, increment the:

1. MAJOR version when you make incompatible API changes,
2. MINOR version when you add functionality in a backwards-compatible manner, and
3. PATCH version when you make backwards-compatible bug fixes.

Additional labels for pre-release and build metadata are available as extensions to the MAJOR.MINOR.PATCH format.

See the Sematic Versioning document for more details.

For MAJOR versions less than 2 (beta), builds should be indicated by the build number and git commit SHA value (short format). For example:

1.3.12-10-5d12c6f

Where:

- 1.3.12 is the MAJOR.MINOR.PATCH version
- -10 is the BUILD number
- -5d12c6f is the git commit SHA value

Build number and git commit SHA value shall not be included on releases 2 or greater.

Version numbering in source code shall be automated by means of a script run at compilation or runtime.

MAJOR and MINOR versions shall be decided by the project/product manager based on completion of project tasks and validation by test.

## 6.3 Reuse/adaptation of Code

Where possible, all embedded firmware code should be developed as modularly as possible to allow for reuse in other (sub) systems. The interface requirements between sub-systems shall remain consistent after the release of the beta version (Major release 2.0.0), requiring all new modules at that time to be backwards compatible.

# Appendix A: Glossary

<Define all the terms necessary to properly interpret the SRS, including acronyms and abbreviations. You may wish to build a separate glossary that spans multiple projects or the entire organization, and just include terms specific to a single project in each SRS.>

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
NOAA – National Oceanic and Atmospheric Administration

O

P

PMEL – Pacific Marine Environmental Laboratory

Q

R

RTOS – Real-time operating system

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
# Appendix B: Analysis Models

<Optionally, include any pertinent analysis models, such as data flow diagrams, class diagrams, state-transition diagrams, or entity-relationship diagrams.>

# Appendix C: To Be Determined List

<Collect a numbered list of the TBD (to be determined) references that remain in the SRS so they can be tracked to closure.>

27 NOAA Pacific Marine Environmental Laboratory - Engineering Development Division

MApC02 Gen2 Version: 0.1 System Requirements Specification Date: August 2, 2017

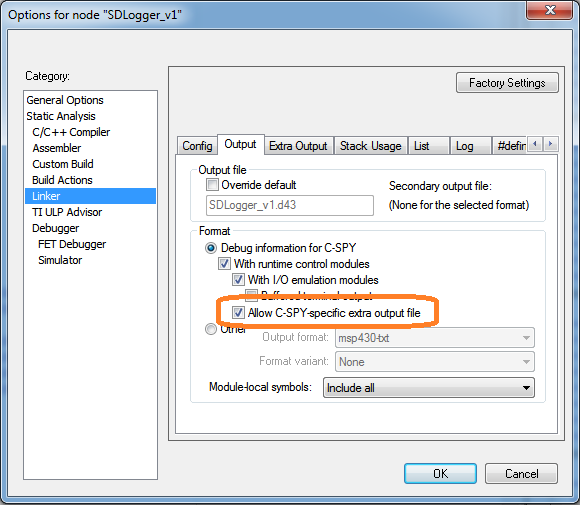
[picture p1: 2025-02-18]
FlowController/Firmware/Binaries/Images/Linker_1.png

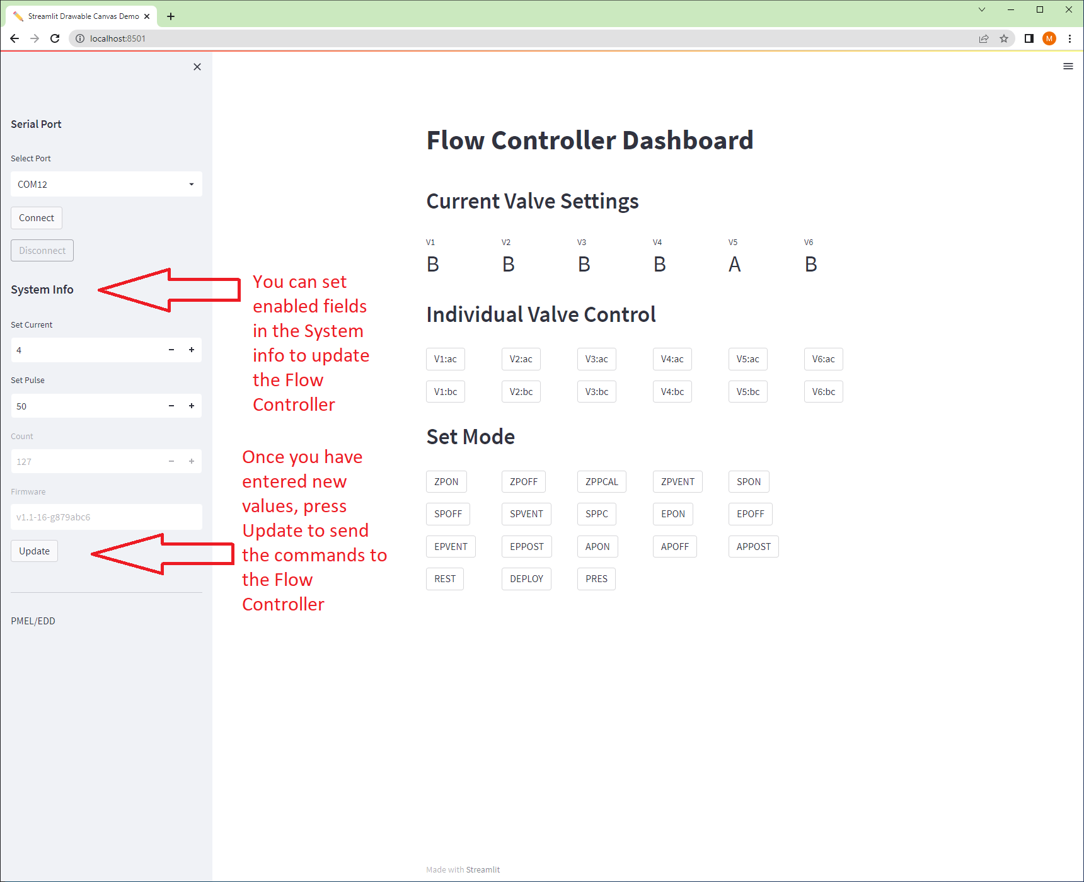
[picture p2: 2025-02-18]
FlowController/Software/FlowControlUI/img/DashboardSystem.png

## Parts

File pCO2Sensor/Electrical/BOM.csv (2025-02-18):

Source: | C:\Users\kurina\Documents\GitHub\EDD-pco2-controller-kicad\pco2-sensor-board\pco2-sensor-board.kicad_sch
Date: | 6/29/2023 15:46
Tool: | Eeschema (7.0.0)
Generator: | C:\Program Files\KiCad\7.0\bin\scripting\plugins/bom_csv_grouped_by_value.py
Component Count: | 168
Collated Components:
Item | Qty | Reference(s) | Value | LibPart | Footprint | Datasheet | DNP | Description | MPN | Notes
1 | 17 | 3V3, 15V1, ANALOG_OUT1, BATT1, FLOW_EN1, FLOW_PWR1, FLOW_SENSE1, LICOR_EN1, LICOR_OUT1, nReset1, SBWTCK1, SENSOR+1, TCK1, TDI1, TDO1, TMS1, VREF_EN1 | TestPoint | Connector:TestPoint | TestPoint:TestPoint_Pad_D1.0mm | ~
2 | 1 | C1 | DHL-5R5D224T | pco2-sensor-board:DHL-5R5D224T | pco2-sensor-board:DHL-5R5D224T | https://eu.mouser.com/datasheet/2/129/dhl_e-5207.pdf |  |  | DHL-5R5D224T
3 | 4 | C6, C15, C83, C84 | 1u | Device:C | Capacitor_SMD:C_0805_2012Metric | ~ |  | 100V | C2012X7S2A105K125AE | 100V
4 | 1 | C7 | 33u | Device:C | Capacitor_SMD:C_1206_3216Metric | ~ |  |  | C2012X5R1A336M125AC
5 | 2 | C8, C10 | 10n | Device:C | Capacitor_SMD:C_0805_2012Metric | ~ |  | 100V | C0805X103K2RAC3316 | 100V
6 | 20 | C9, C20, C21, C26, C55, C56, C60, C80, C81, C82, C96, C97, C98, C99, C100, C101, C102, C103, C104, C105 | 100n | Device:C | Capacitor_SMD:C_0805_2012Metric | ~ |  |  | C0805R104J5RACTU
7 | 8 | C11, C12, C22, C25, C50, C51, C52, C54 | 10u | Device:C | Capacitor_SMD:C_0805_2012Metric | ~ |  | 50V | C2012X5R1H106K125AC | 50V
8 | 1 | C13 | 220n | Device:C | Capacitor_SMD:C_0805_2012Metric | ~ |  |  | C0805C224K1RACTU
9 | 2 | C14, C53 | 47u | Device:C | Capacitor_SMD:C_0805_2012Metric | ~ |  |  | GRM21BR61A476ME15L
10 | 1 | C23 | 100n | pco2-sensor-board:C0805C104M5RACTU | pco2-sensor-board:CAPC2012X88N |  |  |  | C0805R104J5RACTU
11 | 2 | C27, C28 | 100n | Device:C | Capacitor_SMD:C_0603_1608Metric | ~ |  |  | C0805R104J5RACTU
12 | 1 | C30 | 2.2n | pco2-sensor-board:C0805C222K5RACTU | pco2-sensor-board:CAPC2013X88N |  |  |  | C0805C222F5GACTU
13 | 1 | C61 | 47p | Device:C | Capacitor_SMD:C_0805_2012Metric | ~ |  |  | C0805X470F5GACTU
14 | 2 | C85, C91 | 4.7u | Device:C | Capacitor_SMD:C_0805_2012Metric | ~ |  |  | C2012X7R1H475K125AE
15 | 1 | C90 | 10u | Device:C | Capacitor_SMD:C_1210_3225Metric | ~ |  |  | C2012X5R1H106K125AC
16 | 1 | C92 | 91p | Device:C | Capacitor_SMD:C_0805_2012Metric | ~ |  |  | C0805C910J1GACTU
17 | 1 | C93 | 4.7n | Device:C | Capacitor_SMD:C_0805_2012Metric | ~ |  |  | C0805C472K5RACAUTO
18 | 1 | C94 | 110p | Device:C | Capacitor_SMD:C_0805_2012Metric | ~ |  |  | C0805C111J5GACTU
19 | 1 | C95 | 22u | pco2-sensor-board:22u,2917 | pco2-sensor-board:CKG57NX7S1H226M500JH | ~ |  |  | CKG57NX7S1H226M500JH
20 | 2 | FB1, FB10 | MPZ1608S101ATD25 | pco2-sensor-board:MPZ1608S101ATD25 | pco2-sensor-board:MPZ1608S101ATD25 |  |  |  | MPZ1608S101ATD25 | 1kOhm@100MHz
21 | 1 | FL50 | MEM2012F10R0 | pco2-sensor-board:MEM2012F10R0 | pco2-sensor-board:MEM2012F10R0 |  |  |  | MEM2012F10R0
22 | 1 | GRN_LED1 | LGR971-KN-1 | pco2-sensor-board:LGR971-KN-1 | pco2-sensor-board:LGR971-KN-1 |  |  |  | LGR971-KN-1
23 | 4 | H1, H2, H3, H4 | MountingHole | Mechanical:MountingHole | MountingHole:MountingHole_6.4mm_M6 | ~
24 | 4 | J1, J4, J5, J6 | 430450402 | pco2-sensor-board:430450402 | pco2-sensor-board:430450402 |  |  |  | 430450402
25 | 1 | J2 | 430450202 | pco2-sensor-board:430450202 | pco2-sensor-board:430450202 |  |  |  | 430450202
26 | 1 | J7 | 430450602 | pco2-sensor-board:430450602 | pco2-sensor-board:430450602 |  |  |  | 430450602
27 | 1 | JTAG_MINI1 | 3220-10-0100-00 | pco2-sensor-board:3220-10-0100-00 | pco2-sensor-board:3220-10-0100-00 |  |  |  | 3220-10-0100-00
28 | 1 | L9 | 33uH | pco2-sensor-board:MSP430FR5994IPNR | pco2-sensor-board:7443551331 | http://componentsearchengine.com/Datasheets/1/7443551331.pdf |  | SMD-Flat Wire High Current Inductor WE-HCI | 7443551331
29 | 1 | L11 | 220u | pco2-sensor-board:VLCF4028T-220MR72-2 | pco2-sensor-board:VLCF4028T-220MR72-2 |  |  |  | VLCF4028T-220MR72-2
30 | 1 | PF1 | NANOSMDC020F | pco2-sensor-board:NANOSMDC020F | pco2-sensor-board:NANOSMDC020F-2 |  |  |  | NANOSMDC020F
31 | 2 | PF7, PF81 | 0ZCG0075FF2C | pco2-sensor-board:0ZCG0075FF2C | pco2-sensor-board:0ZCG0075FF2C |  |  |  | 0ZCG0075FF2C
32 | 1 | Q1 | SI1330EDL-T1-GE3 | pco2-sensor-board:SI1330EDL-T1-GE3 | pco2-sensor-board:SI1330EDL-T1-GE3 | ~ |  |  | SI1330EDL-T1-GE3
33 | 23 | R2, R3, R4, R5, R6, R8, R10, R15, R84, R85, R86, R87, R88, R95, R96, R97, R98, R99, R100, R101, R102, R103, R104 | 100 | Device:R | Resistor_SMD:R_0805_2012Metric | ~ |  |  | CRCW0805100RFKEAC
34 | 2 | R7, R24 | 1k | Device:R | Resistor_SMD:R_0805_2012Metric | ~ |  |  | CRCW08051K00FKEAC
35 | 2 | R9, R91 | 71.5k | Device:R | Resistor_SMD:R_0805_2012Metric | ~ |  |  | CRCW080571K5FKEA
36 | 1 | R11 | 226k | Device:R | Resistor_SMD:R_0805_2012Metric | ~ |  |  | CRCW0805226KFKEA
37 | 2 | R12, R92 | 1M | Device:R | Resistor_SMD:R_0805_2012Metric | ~ |  |  | CRCW08051M00FKEAC
38 | 1 | R13 | 200k | Device:R | Resistor_SMD:R_0805_2012Metric | ~ |  |  | CRCW0805200KFKEAC
39 | 2 | R14, R94 | 1 | Device:R | Resistor_SMD:R_0805_2012Metric | ~ |  |  | CRCW08051R00FKEAC
40 | 11 | R20, R21, R31, R33, R109, R110, R111, R112, R113, R114, R115 | 10k | Device:R | Resistor_SMD:R_0805_2012Metric | ~ |  |  | CRCW080510K0FKEAC
41 | 1 | R22 | 10.7k | Device:R | Resistor_SMD:R_0805_2012Metric | ~ |  |  | CRCW080510K7FKEAC
42 | 1 | R23 | 309k | Device:R | Resistor_SMD:R_0805_2012Metric | ~ |  |  | CRCW0805309KFKEA
43 | 1 | R30 | 30k | Device:R | Resistor_SMD:R_0805_2012Metric | ~ |  |  | CRCW080530K0FKEAC
44 | 1 | R32 | 100k | Device:R | Resistor_SMD:R_0805_2012Metric | ~ |  |  | CRCW0805100KFKEAC
45 | 1 | R34 | 47k | Device:R | Resistor_SMD:R_0805_2012Metric | ~ |  |  | CRCW080547K0FKEAC
46 | 2 | R50, R51 | 330 | Device:R | Resistor_SMD:R_0805_2012Metric | ~ |  |  | CRCW0805330RFKEAC
47 | 1 | R52 | 470 | Device:R | Resistor_SMD:R_0805_2012Metric | ~ |  |  | CRCW0805470RFKEAC
48 | 1 | R60 | 1.5k | Device:R | Resistor_SMD:R_0805_2012Metric | ~ |  |  | CRCW08051K50FKEAC
49 | 1 | R80 | 470k | Device:R | Resistor_SMD:R_0805_2012Metric | ~ |  |  | CRCW0805470KFKEAC
50 | 1 | R81 | 49.9k | Device:R | Resistor_SMD:R_0805_2012Metric | ~ |  |  | CRCW080549K9FKEAC
51 | 1 | R90 | 24.9k | Device:R | Resistor_SMD:R_0805_2012Metric | ~ |  |  | CRCW080524K9FKEAC
52 | 1 | R93 | 20k | Device:R | Resistor_SMD:R_0805_2012Metric | ~ |  |  | CRCW080520K0FKEAC
53 | 4 | R105, R106, R107, R108 | 4.7k | Device:R | Resistor_SMD:R_0805_2012Metric | ~ |  |  | CRCW08054K70FKEAC
54 | 1 | RED_LED1 | LS R976-NR-1 | pco2-sensor-board:LSR976-NR-1 | pco2-sensor-board:LGR971-KN-1 |  |  |  | LS R976-NR-1
55 | 1 | U1 | LT3970EMS-3.3-PBF | pco2-sensor-board:LT3970EMS-3.3-PBF | pco2-sensor-board:LT3970EMS-3.3-PBF |  |  |  | LT3970EMS-3.3-PBF
56 | 1 | U2 | LT1672IS8-PBF | pco2-sensor-board:LT1672IS8-PBF | pco2-sensor-board:LT1672IS8-PBF |  |  |  | LT1672IS8-PBF
57 | 1 | U3 | TPL5010DDCR | pco2-sensor-board:TPL5010DDCR | pco2-sensor-board:TPL5010DDCR |  |  |  | TPL5010DDCR
58 | 1 | U5 | MSP430FR5994IPNR | pco2-sensor-board:MSP430FR5994IPNR | pco2-sensor-board:MSP430FR5994IPNR |  |  |  | MSP430FR5994IPNR
59 | 1 | U6 | AB0805-T3 | pco2-sensor-board:AB0805-T3 | pco2-sensor-board:QFN50P300X300X90-17N |  |  |  | AB0805-T3
60 | 1 | U7 | AQY211G2SX | pco2-sensor-board:AQY211G2SX | pco2-sensor-board:AQY211G2SX |  |  |  | AQY211G2SX
61 | 1 | U8 | MAX3109ETJ+ | pco2-sensor-board:MAX3109ETJ+ | pco2-sensor-board:MAX3109ETJ+ |  |  |  | MAX3109ETJ+
62 | 1 | U9 | LTC3115IDHD-1-PBF | pco2-sensor-board:LTC3115IDHD-1-PBF | pco2-sensor-board:LTC3115IDHD-1-PBF |  |  |  | LTC3115IDHD-1-PBF
63 | 2 | U11, U80 | MAX3224EETP+ | pco2-sensor-board:MAX3224EETP+ | pco2-sensor-board:MAX3224EETP+ |  |  |  | MAX3224EETP+
64 | 1 | U20 | ISL60002BIH310Z-TK | pco2-sensor-board:ISL60002BIH310Z-TK | pco2-sensor-board:ISL60002BIH310Z-TK |  |  |  | ISL60002BIH310Z-TK
65 | 1 | U21 | BME280 | pco2-sensor-board:BME280 | pco2-sensor-board:BME280 | https://datasheet.datasheetarchive.com/originals/distributors/DKDS-24/462906.pdf |  |  | BME280
66 | 1 | U30 | SN74LVC1G240DBVR | pco2-sensor-board:SN74LVC1G240DBVR | pco2-sensor-board:SN74LVC1G240DBVR |  |  |  | SN74LVC1G240DBVR
67 | 1 | U50 | SG-210STF 7.3728ML | pco2-sensor-board:SG-210STF 7.3728ML | pco2-sensor-board:SG-210STF 7.3728ML |  |  |  | SG-210STF 7.3728ML
68 | 1 | U81 | LDL212DR | pco2-sensor-board:LDL212DR | pco2-sensor-board:LDL212DR |  |  |  | LDL212DR
69 | 1 | Y60 | ABS06-107-32.768KHZ-T | pco2-sensor-board:ABS06-107-32.768KHZ-T | pco2-sensor-board:ABS0610732768KHZT | http://www.abracon.com/Resonators/ABS06-107-32.768kHz-T.pdf |  | ABRACON - ABS06-107-32.768KHZ-T - CRYSTAL, 32.768KHZ, 4PF, 2 X 1.2MM | ABS06-107-32.768KHZ-T
70 | 1 | Y80 | ABLS-3.6864MHZ-B4-T | pco2-sensor-board:ABLS-3.6864MHZ-B4-T | pco2-sensor-board:ABLS-3.6864MHZ-B4-T |  |  |  | ABLS-3.6864MHZ-B4-T

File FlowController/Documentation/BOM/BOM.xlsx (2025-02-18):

BOM |  | ASVCO2 Flow Controller
Item | Qty | Reference(s) | Value | MPN | Digikey PN
1 | 4 | C1, C8, C9, C10 | 10uF | CL10A106MQ8NNNC | CL10A106MQ8NNNC
2 | 12 | C2, C3, C5, C14, C15, C19, C20, C22, C23, C24, C25, C26 | 0.1uF | C0603X104K5RAC7867 | C0603X104K5RACTU
3 | 1 | C4 | 0.22uF | CGA3E3X7R1H224K080AB | CGA3E3X7R1H224K080AB
4 | 1 | C6 | 10uF | CGA5L1X7R1E106K160AE | CGA5L1X7R1E106K160AE
5 | 1 | C7 | 47uF | LMK325B7476MM-TR | LMK325B7476MM-TR
6 | 1 | C11 | 47uF | KGM15BR71E473KT | KGM15BR71E473KT
7 | 2 | C12, C17 | 0.47uF | CGA3E3X7R1H474K080AE | CGA3E3X7R1H474K080AE
8 | 2 | C13, C18 | 0.01uF | C0603C103K2RACTU | C0603C103K2RACTU
9 | 2 | C16, C21 | 0.33mF | URZ1H331MHD1TO | URZ1H331MHD1TO
10 | 1 | C27 | 10nF | C0603X103J4HACTU | C0603X103J4HACTU
11 | 1 | D1 | S1B-F-2 | S1B-13-F | S1B-13-F
12 | 1 | J1 | VALVE 1 | SSW-102-01-F-S | SSW-102-01-F-S
13 | 1 | J2 | VALVE 2 | SSW-102-01-F-S | SSW-102-01-F-S
14 | 1 | J3 | VALVE 3 | SSW-102-01-F-S | SSW-102-01-F-S
15 | 1 | J4 | VALVE 4 | SSW-102-01-F-S | SSW-102-01-F-S
16 | 1 | J5 | VALVE 5 | SSW-102-01-F-S | SSW-102-01-F-S
17 | 1 | J6 | VALVE 6 | SSW-102-01-F-S | SSW-102-01-F-S
18 | 1 | J7 | 3220-10-0100-00 | 3220-10-0100-00 | 3220-10-0100-00
19 | 1 | J8 | PUMP | 430450202 | WM1819-ND
20 | 1 | J9 | 430450402 | 430450402 | WM1820-ND
21 | 1 | L1 | VLCF4028T-220MR72-2 | VLCF4028T-220MR72-2 | VLCF4028T-220MR72-2
22 | 1 | R1 | 226k | ERJ-3EKF2263V | ERJ-3EKF2263V
23 | 1 | R2 | 470R | ESR03EZPJ471 | ESR03EZPJ471
24 | 6 | R3, R4, R5, R6, R8, R9 | 0.5R | RL0603FR-070R5L | RL0603FR-070R5L
25 | 2 | R7, R10 | 120R | ESR03EZPJ121 | ESR03EZPJ121
26 | 1 | R11 | 1k | RT0603BRD071KL | RT0603BRD071KL
27 | 1 | R12 | 47k | RC0603JR-1347KL | RC0603JR-1347KL
28 | 1 | U1 | MSP430FR5994IPNR | MSP430FR5994IPNR | MSP430FR5994IPNR
29 | 1 | U2 | LT3970EMS-3.3-PBF | LT3970EMS-3.3#PBF | 505-LT3970EMS-3.3#PBF-ND
30 | 1 | U3 | MEM2012F10R0 | MEM2012F10R0 | 445-MEM2012F10R0TR-ND
31 | 1 | U4 | SG-8018CG 7.3728M-TJHSA0 | SG-8018CG 7.3728M-TJHSA0 | SG-8018CG7.3728M-TJHSA0-ND
32 | 2 | U5, U6 | DRV8823QDCARQ1 | DRV8823QDCARQ1 | 296-40077-2-ND
33 | 1 | U7 | LTST-C195KGJRKT | LTST-C195KGJRKT | 160-1452-2-ND
34 | 1 | U8 | MAX3224EETP+ | MAX3224EETP+ | MAX3224EETP+-ND
35 | 1 | U9 | AQY282S | AQY282S | 255-1795-5-ND

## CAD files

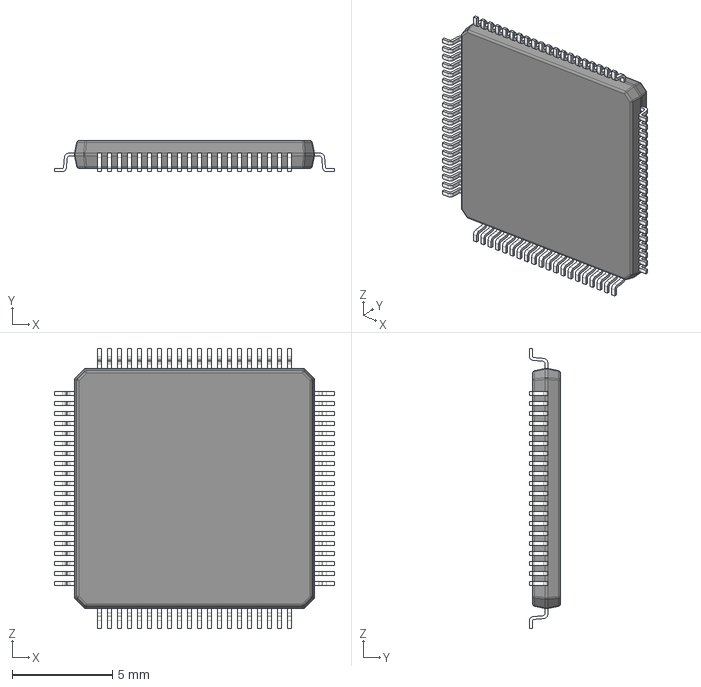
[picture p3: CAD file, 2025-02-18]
pCO2Sensor/Electrical/models/MSP430FR5994IPNR.step
14.0 x 1.56 x 14.0 mm
BODY_VHB80A
LEAD_VHB80A x 80

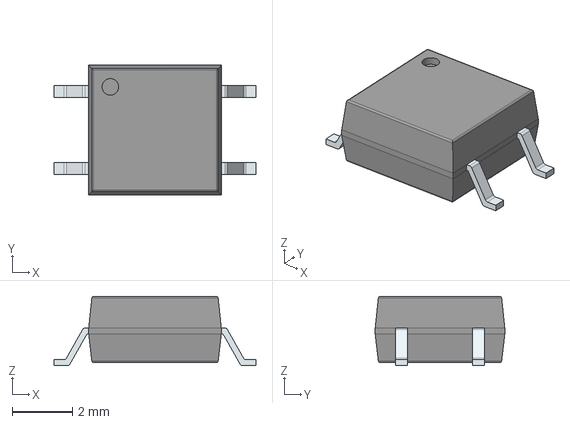
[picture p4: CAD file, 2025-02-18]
pCO2Sensor/Electrical/models/AQY211G2SX.stp
6.70 x 4.30 x 2.30 mm
PinsArrayLR

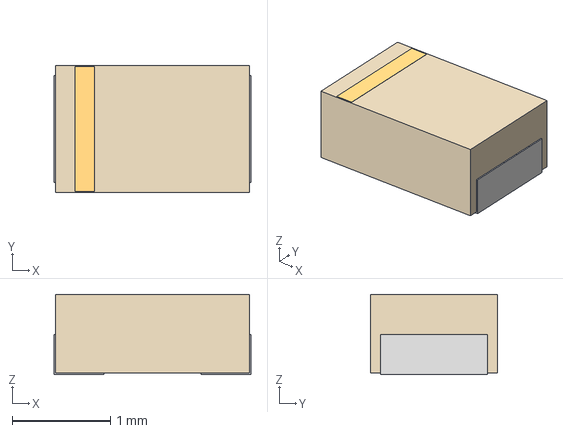
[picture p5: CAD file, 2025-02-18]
pCO2Sensor/Electrical/models/LSR976-NR-1.step
2.01 x 1.30 x 0.815 mm

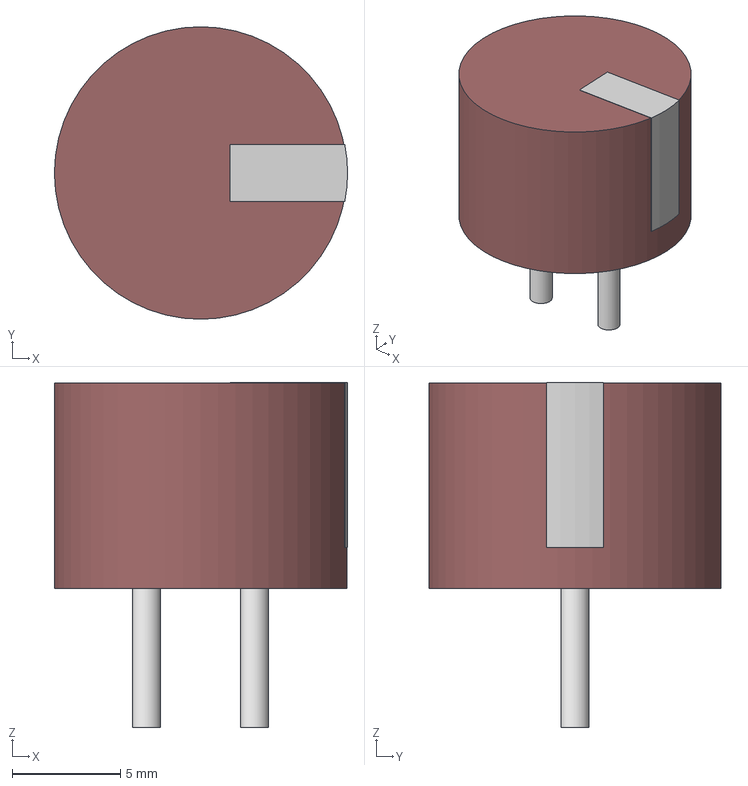
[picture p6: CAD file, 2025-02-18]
pCO2Sensor/Electrical/models/cap_DHL5R5D_ELN.step
13.5 x 13.5 x 15.9 mm

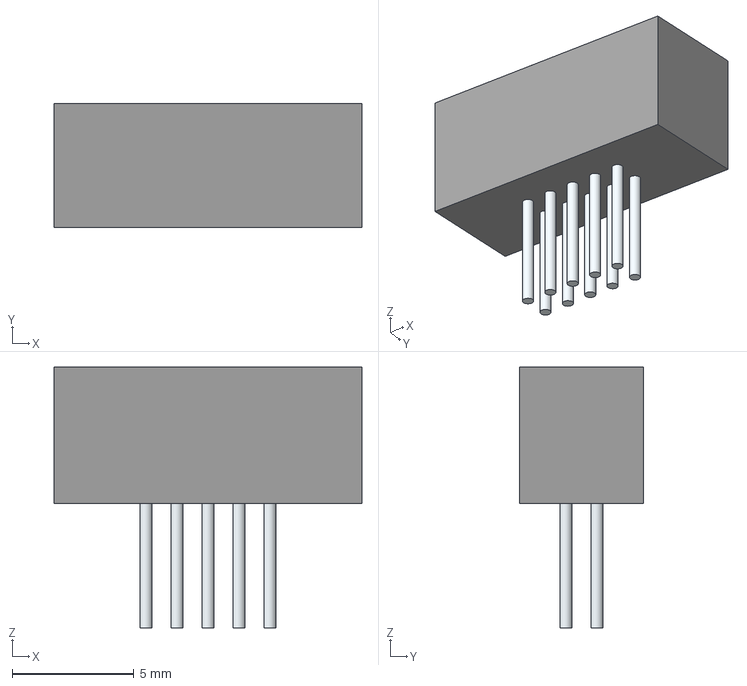
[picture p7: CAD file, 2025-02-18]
pCO2Sensor/Electrical/models/3220-10-0100-00.stp
12.7 x 5.10 x 10.7 mm
Leads

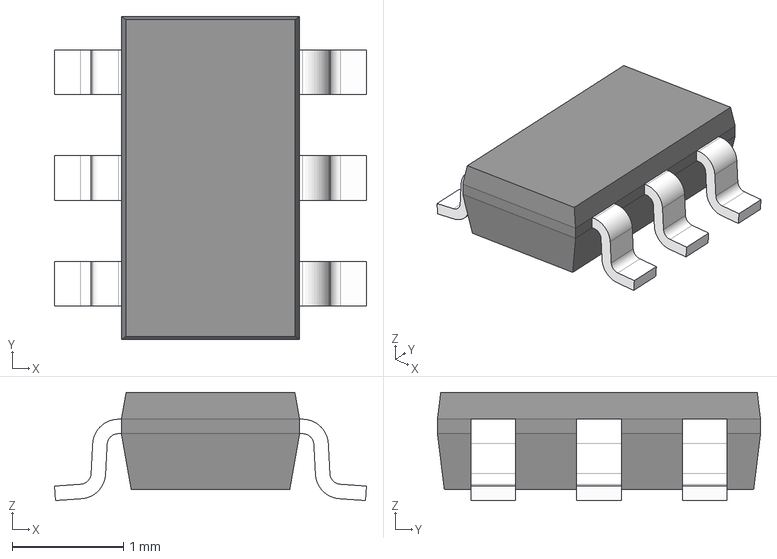
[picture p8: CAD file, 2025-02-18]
pCO2Sensor/Electrical/models/DDC0006A.stp
2.80 x 2.90 x 0.97 mm
BODY-SOT
LEAD-SOT x 6

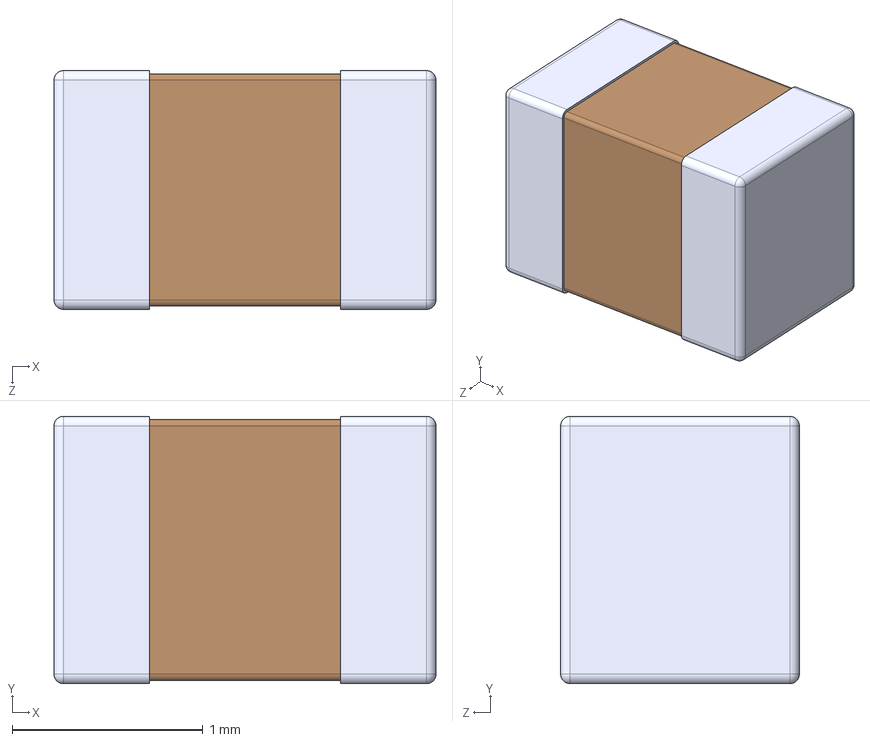
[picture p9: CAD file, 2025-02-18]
pCO2Sensor/Electrical/models/C0805C224K5RACTU.step
2.00 x 1.40 x 1.25 mm

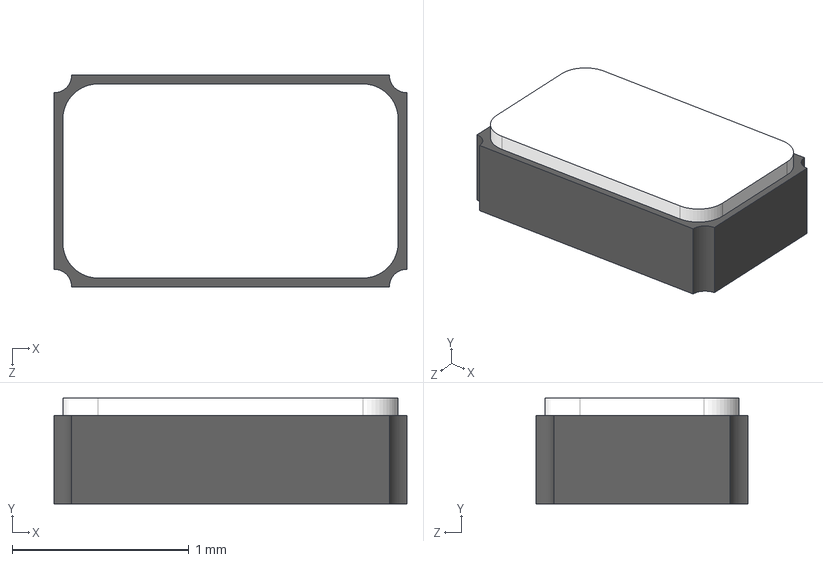
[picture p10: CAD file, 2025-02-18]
pCO2Sensor/Electrical/models/ABS06-107-32.768KHZ-T.stp
2.00 x 0.6 x 1.20 mm

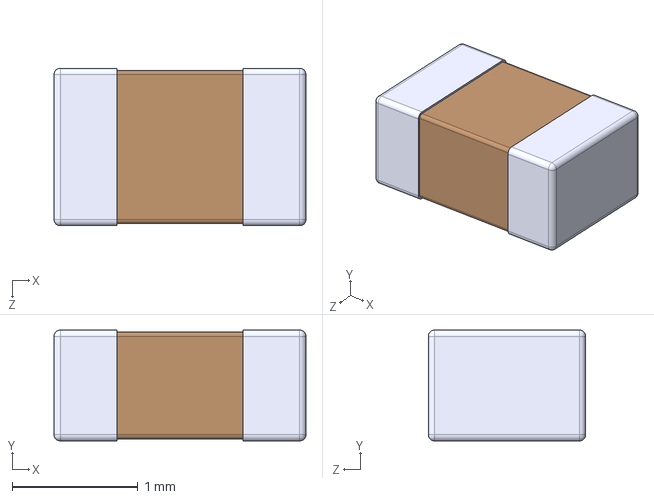
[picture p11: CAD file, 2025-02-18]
pCO2Sensor/Electrical/models/C0805C103K1RACAUTO.stp
2.00 x 0.88 x 1.25 mm

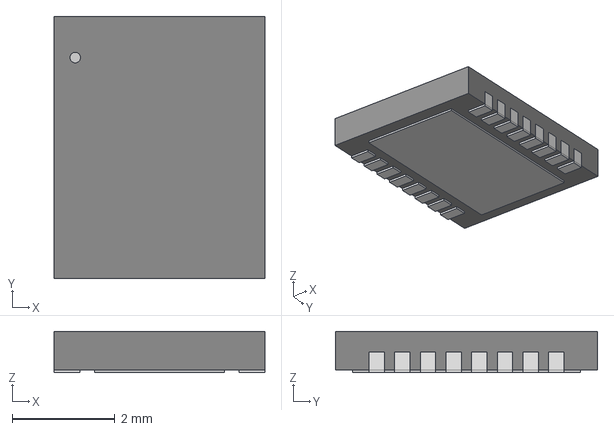
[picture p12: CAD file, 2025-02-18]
pCO2Sensor/Electrical/models/LTC3115IDHD-1-PBF.step
4.10 x 5.10 x 0.803 mm

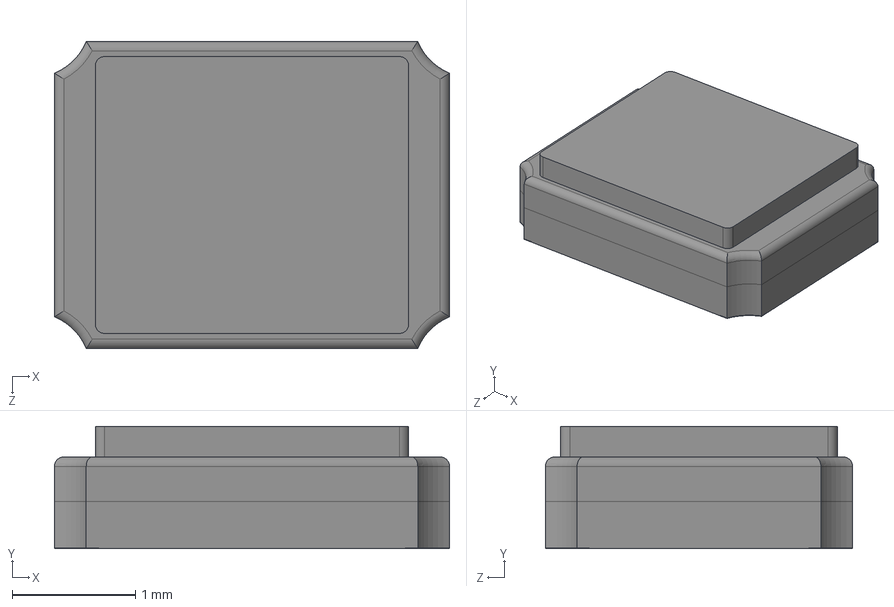
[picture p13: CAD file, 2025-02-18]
pCO2Sensor/Electrical/models/ASE-7.3728MHZ-LC-T.step
3.20 x 0.991 x 2.49 mm

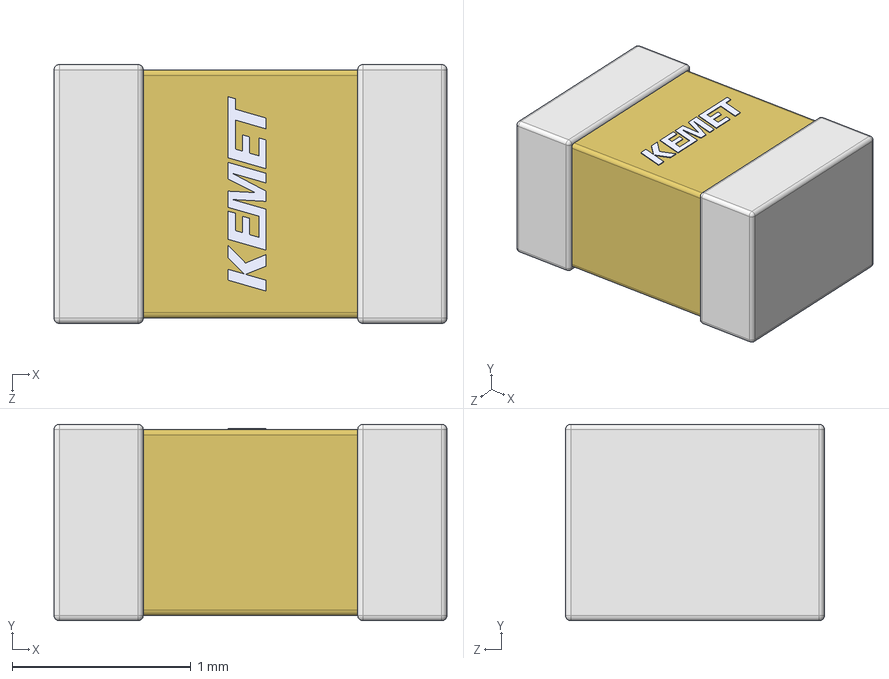
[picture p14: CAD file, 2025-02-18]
pCO2Sensor/Electrical/models/CCS_CCSTD_0805_L2.2W1.45T1.1B0.5.step
2.20 x 1.10 x 1.45 mm

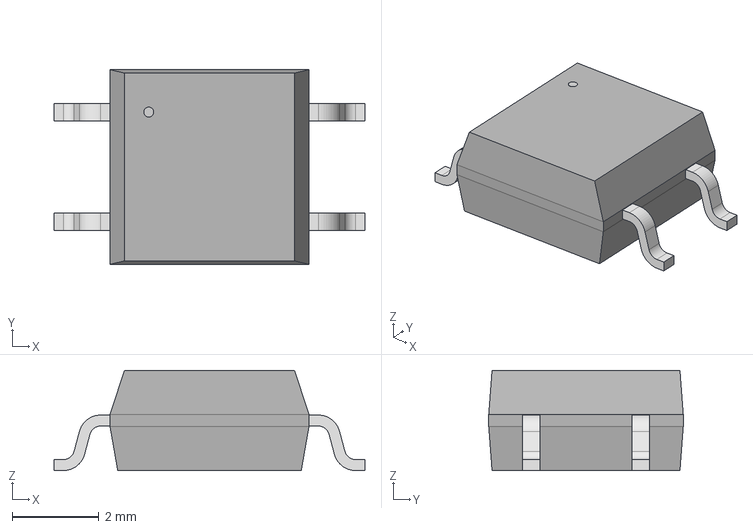
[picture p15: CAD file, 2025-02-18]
pCO2Sensor/Electrical/models/GU_SOP4_PAN.step
7.19 x 4.50 x 2.31 mm

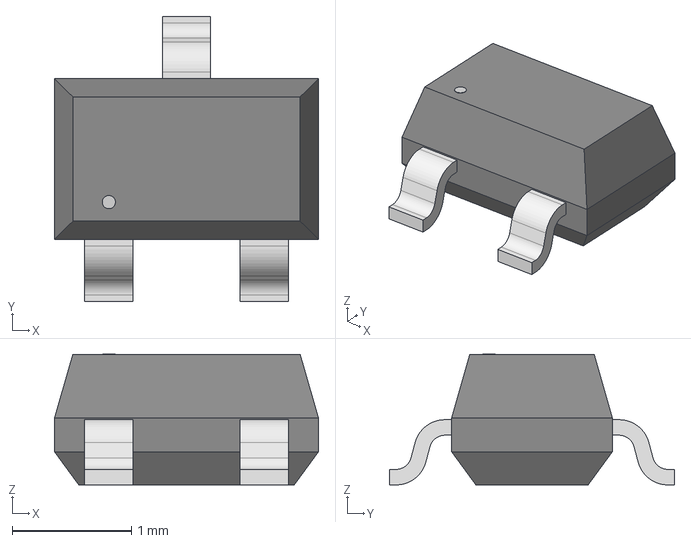
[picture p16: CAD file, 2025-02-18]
pCO2Sensor/Electrical/models/SI1330EDL-T1-GE3.step
2.21 x 2.39 x 1.09 mm

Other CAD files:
pCO2Sensor/Electrical/models/MEM2012F10R0.step
pCO2Sensor/Electrical/models/DHL-5R5D224T.stp
pCO2Sensor/Electrical/models/0ZCG0075FF2C.stp
pCO2Sensor/Electrical/models/21-0140_T32554_MXM.step
pCO2Sensor/Electrical/models/43045-0202.stp
pCO2Sensor/Electrical/models/43045-0402.stp
pCO2Sensor/Electrical/models/43045-0602.stp
pCO2Sensor/Electrical/models/7443551331.stp
pCO2Sensor/Electrical/models/AB0805-T3.stp
pCO2Sensor/Electrical/models/ABLS-3.6864MHZ-B4-T.step
pCO2Sensor/Electrical/models/AC0805JR-07200KL.stp
pCO2Sensor/Electrical/models/ACML-0805.STEP
pCO2Sensor/Electrical/models/ADUM3160BRWZ.stp
pCO2Sensor/Electrical/models/APT2012LVBC_D.stp
pCO2Sensor/Electrical/models/BME280.stp
pCO2Sensor/Electrical/models/C0805C222K5RACTU.stp
pCO2Sensor/Electrical/models/CAPC220145_88N_KEM.step
pCO2Sensor/Electrical/models/CAP_2012_TDK.step
pCO2Sensor/Electrical/models/CAP_3216_TDK.step
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

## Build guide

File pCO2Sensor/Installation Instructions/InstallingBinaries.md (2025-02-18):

# MSP430 Programming Instructions

PMEL's Engineering Development Division uses MSP430 microcontrollers in many of
the custom circuits.  The following is the procedure for programming the
microcontrollers, also known as "flashing".

## Requirements
The following are the basic hardware and software requirements for loading
binary files onto the microcontroller.

### Hardware
* Texas Instruments MSP-FET Flash Emulation Tool
* EDD Custom 0.100" Pitch x14-pin to 0.050" pitch x10-pin converter

### Software
* Elprotronic, Inc. FET-Pro-430-LITE
  * Free download from www.elprotronic.com

### Files
* Pre-generated binary files for target device
  * File should have the form "DeviceName_version.txt

## Loading "Binary" files to target
  1. Connect the programming cable to the microcontroller and the MSP-FET.
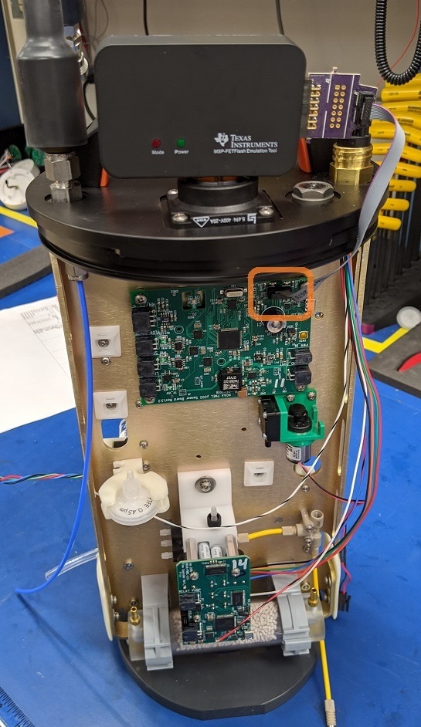
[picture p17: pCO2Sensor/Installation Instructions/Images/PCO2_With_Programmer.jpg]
  

  1. Apply Power to the target board

  1. Open the FET-Pro-430 program

  1. Press the button "Open Code File ->", navigate to the location of the "binary"
  file (ProjectName.txt)
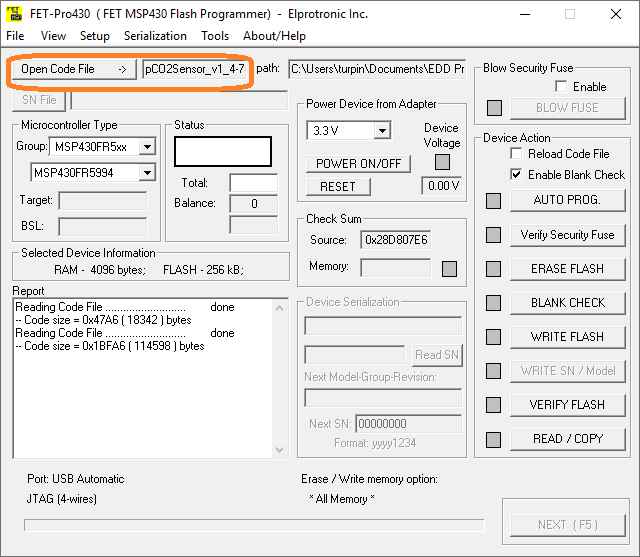
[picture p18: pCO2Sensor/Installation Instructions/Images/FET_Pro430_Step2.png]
  

  1. In the Microcontroller Type block (refer to User Manual for values)
    * In "Group", select the general type of MSP430 used.
    * On the next line, select the specific type of MSP430 used
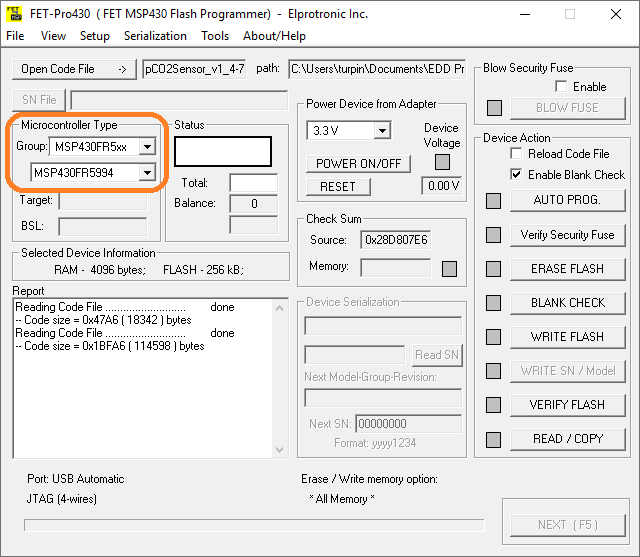
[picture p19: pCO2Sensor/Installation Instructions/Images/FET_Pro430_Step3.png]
  

  1. In the "Device Action" block, press "AUTO PROG."
    * If successfull, the "Status" block should show **"Pass"**
    * If unsuccessfull, press "ERASE FLASH" and try step 6 again.
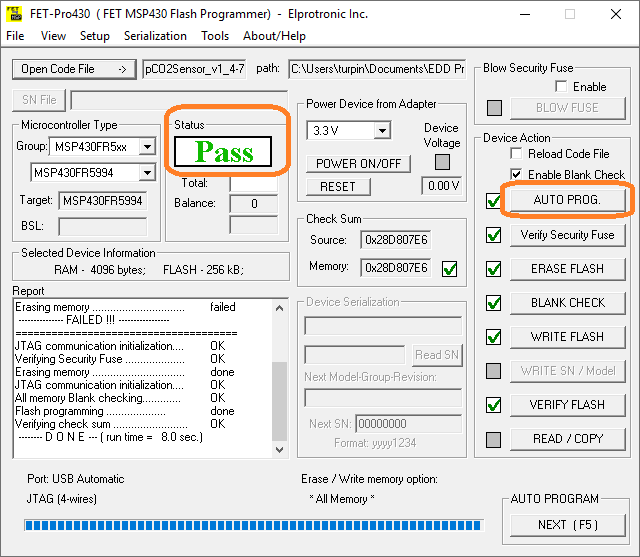
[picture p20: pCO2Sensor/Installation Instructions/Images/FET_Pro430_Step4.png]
  

  1. The device is now programmed. Pressing the reset switch or power cycling the instrument will allow console communication.

  **NOTE:** The board may require additional configuration settings over the
    console.  Consult the User Manual for the corresponding device.

## Reloading System Parameters
  
### Serial Number
  1. The ASVCO2 Gen 2 System number needs to be re-entered with this command: "serial= xxxx\r\n" (Note: This number can be found on the ASVCO2 label on the system's endcap)
  
### RTC Calibration
  1. From the ASVCO2 Command Prompt send command "rtccal\r\n" 

  1. From Page 5 of the ASVCO2 Gen 2 Build Checklist, enter the value from step 3.19.2 
  
  1. If the buildlist is not available, use a frequency counter to measure the frequency output on the RTC header JB6. Input the value from the counter to two decimal places (Example: "32768.00\r\n").
  
### SPAN Gas Concentration
  1. The span gas concentration needs to be re-entered with command "span= xxx.yy\r\n"  (note the space between "=" and the value). 
  
  1. The second span concentration needs to updated only if a span2 calibration is required. Typically this is not required for normal operation.

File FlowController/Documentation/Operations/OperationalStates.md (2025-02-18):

# pCO2 Operational States
## Overview
The following are the operation flow control states for the MApCO2 system.

## Operation State

| State | Description | Cycle | Command |Pump | V1 | V2 | V3 | V4 | V5 | V6 |
|-------|-------------|------------|--------------|-----|----|----|----|----|----|----|
| 1 | Zero Pump ON | Zero | ZPON | ON | CB | CB | CB | CB | CA | CB |
| 2 | Zero Pump OFF | Zero | ZPOFF | OFF | CB | CB | CB | CB | CA | CB |
| 3 | Zero Vent | Zero | ZPVENT | OFF | CB | CB | CB | CA | CA | CB |
| 4 | Zero Post | Zero | ZPPCAL | OFF | CB | CB | CB | CB | CA | CB |
| 5 | Span Flow ON | SPAN | SPON | OFF | CA | CB | CB | CA | CB | CB |
| 6 | Span Flow OFF | SPAN | SPOFF | OFF | CA | CB | CB | CA | CA | CB |
| 7 | Span Vent | SPAN | SPVENT | OFF | CA | CB | CB | CA | CA | CB |
| 8 | Span Post | SPAN | SPPCAL | OFF | CA | CB | CB | CB | CA | CB |
| 9 | Equil Pump ON | EQUIL | EPON | ON | CB | CA | CA | CB | CA | CA |
| 10 | Equil Pump OFF | EQUIL | EPOFF | OFF | CB | CA | CA | CB | CA | CA | 
| 11 | Equil Vent | EQUIL | EPVENT | OFF | CA | CB | CB | CA | CA | CA | CA |
| 12 | Equil Post | EQUIL | EPPOST | OFF | CA | CB | CB | CA | CA | CA | CA |
| 13 | Air Pump ON | AIR | APON | ON | CA | CB | CB | CA | CA | CA |
| 14 | Air Pump OFF | AIR | APOFF | OFF | CA | CB | CB | CA | CA | CA |
| 15 | Air Vent | AIR | APVENT | OFF | CA | CB | CB | CA | CA | CA | 
| 16 | Air Post | AIR | APPOST | OFF | CA | CB | CB | CA | CA | CA |
| 17 | Rest | REST | REST | OFF | CB | CB | CB | CB | CA | CB |
| 18 | Purge 1 | PURGE | PRG1 | ON | CA | CB | CA | CB | CA | CA |
| 19 | Purge 2 | PURGE | PRG2 | OFF | CB | CA | CA | CB | CB | CA |
| 20 | Purge 3 | PURGE | PRG3 | OFF | CB | CA | CB | CA | CA | CA |
| 21 | Purge 4 | PURGE | PRG4 | OFF | CB | CB | CB | CA | CA | CA |
| 22 | Purge 5 | PURGE | PRG5 | OFF | CA | CB | CB | CA | CA | CA |
| 23 | Purge 6 | PURGE | PRG6 | OFF | CB | CB | CB | CB | CA | CB |
| 24 | Purge 7 | PURGE | PRG7 | OFF | CB | CB | CB | CA | CB | CB |
| 25 | Purge 8 | PURGE | PRG8 | OFF | CA | CB | CB | CA | CA | CB |

## Deployment State
| State | Description |  State Name | Command|Pump | V1 | V2 | V3 | V4 | V5 | V6 |
|-------|-------------|-------------|--------|-----|----|----|----|----|----|----|
| 1 | Deployment Mode | Deploy | DEPLOY | Off | CB | CB | CB | CB | CA | CA |

## Experimental
| State | Description | Cycle | Command |Pump | V1 | V2 | V3 | V4 | V5 | V6 |
|-------|-------------|------------|--------------|-----|----|----|----|----|----|----|
| 1 | Pressurize | PRES | PRES | ON | CA | CB | CB | CB | CA | CB |

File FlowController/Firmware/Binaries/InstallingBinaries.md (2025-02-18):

# MSP430 Programming Instructions

PMEL's Engineering Development Division uses MSP430 microcontrollers in many of
the custom circuits.  The following is the procedure for programming the
microcontrollers, also known as "flashing".

## Requirements
The following are the basic hardware and software requirements for loading
binary files onto the microcontroller.

### Hardware
* Texas Instruments MSP-FET Flash Emulation Tool
* EDD Custom 0.100" Pitch x14-pin to 0.050" pitch x10-pin converter

### Software
* Elprotronic, Inc. FET-Pro-430-LITE
  * Free download from www.elprotronic.com

### Files
* Pre-generated binary files for target device
  * File should have the form "DeviceName_version.txt

## Loading "Binary" files to target
  1. Connect the programming cable to the microcontroller and the MSP-FET.

  2. Apply Power to the target board

  3. Open the FET-Pro-430 program

  4. Press the button "Open Code File ->", navigate to the location of the "binary"
  file (ProjectName.txt)

    * In the source code project folder, this is found in Debug->Exe->Projectname.txt

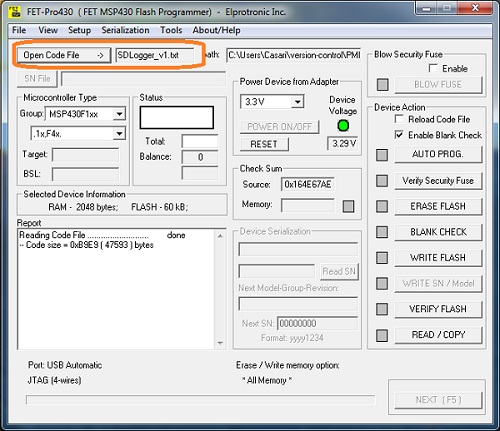
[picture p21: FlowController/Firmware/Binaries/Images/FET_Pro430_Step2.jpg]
    

  5. In the Microcontroller Type block (refer to User Manual for values)
    * In "Group", select the general type of MSP430 used.
    * On the next line, select the specific type of MSP430 used

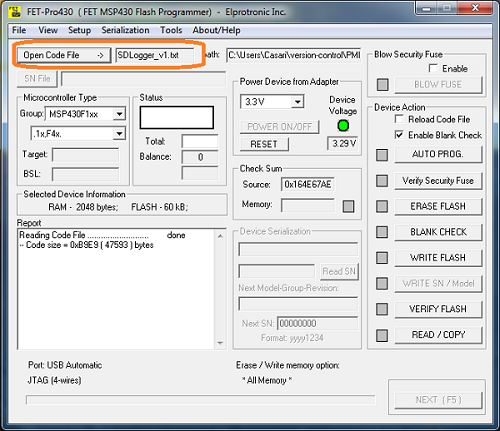
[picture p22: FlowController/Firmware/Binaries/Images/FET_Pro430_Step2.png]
    

  6. In the "Device Action" block, press "AUTO PROG."
    * If successfull, the "Status" block should show **"Pass"**
    * If unsuccessfull, press "ERASE FLASH" and try step 6 again.

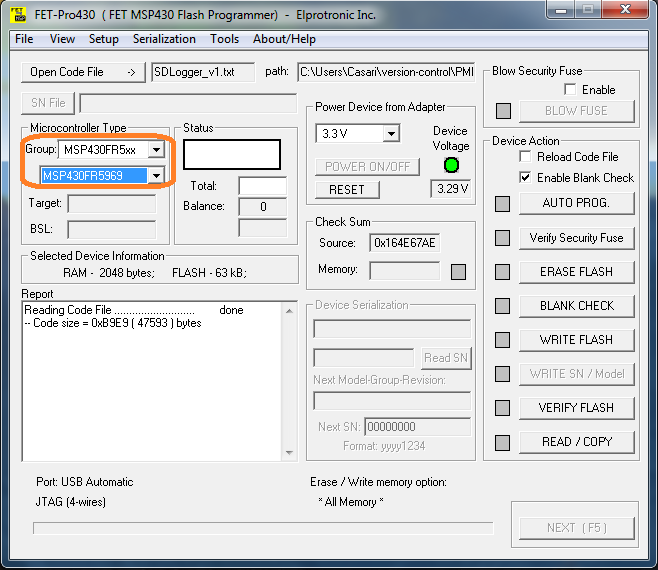
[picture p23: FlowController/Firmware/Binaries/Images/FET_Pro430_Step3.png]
    

  7. The device is now programmed

    * **NOTE:** The board may require additional configuration settings over the
    console.  Consult the User Manual for the corresponding device.

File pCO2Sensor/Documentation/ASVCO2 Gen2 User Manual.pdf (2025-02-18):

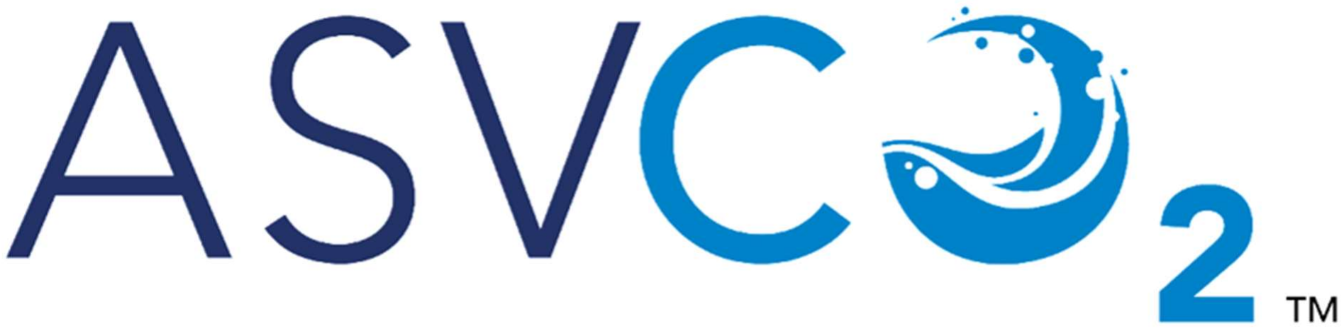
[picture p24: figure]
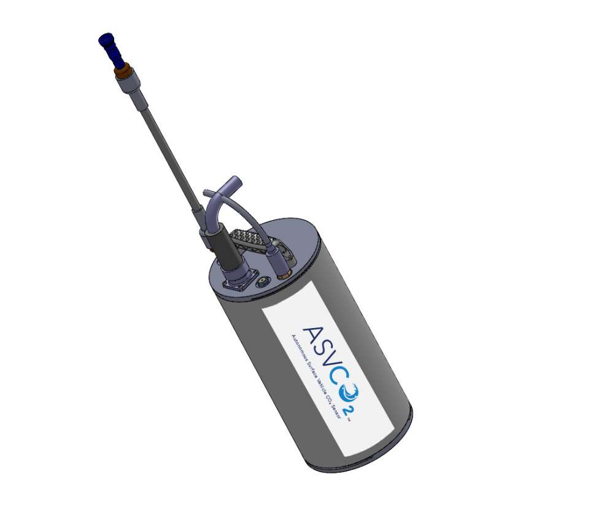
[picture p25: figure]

# ASVCO2 GEN 2 USER MANUAL

07.23.2023

## Engineering Development Division

### NOAA Pacific Marine Environmental Laboratory

### 7600 Sand Point Way NE

### Building 3/EDD

### Seattle, WA 98115

1

# REVISION HISTORY

NAME | DATE | CHANGES | FW VERSION
M. Casari | 7/18/2019 | First release | 1.0
M. Casari | 8/5/2019 | New error code and FLAGS field formatting | 1.1
M. Casari | 8/9/2019 | Flow Control Auto-Recovery added | 1.2
M. Casari | 8/23/2019 | New States and Timing | 1.3
M. Casari | 8/23/2019 | Changes to latest states & timings | 1.4
M. Casari | 3/18/2021 | Updating coefficients naming. Adding tsq mode. | 1.7
M. Casari | 3/29/2021 | Changing Mode to State. Add Flow Diagrams. More detail on Error/Flags. | 1.7
M. Casari | 4/13/2021 | Multiple changes to report, menu. Adding sdata & idata. | 1.8
M. Casari | 8/8/2021 | NetCDF Template Notes, Manufacturer data | 1.8-13
M. Casari | 9/14/2021 | Baud rate changes, ATRH auto-populated serial number, | 1.9
M. Casari | 7/22/2022 | Idata and sdata updates. Sample rate updated. SPON time now settable. | 1.10
M. Casari | 7/21/2023 | Purge cycles added. New method for logging. | 1.11

2

# Overview

There is a current need to quantify the daily to inter-annual variability in air-sea CO2 fluxes and understand the mechanisms controlling these fluxes. The carbon group at the Pacific Marine Environmental Laboratory (PMEL) within the National Oceanic and Atmospheric Administration (NOAA) has mounted sensors on moored buoys to provide high resolution time-series measurements of atmospheric boundary layer and surface pCO2. This data is used to evaluate the temporal variability in air-sea CO2 fluxes and to assist in examining the mechanisms controlling CO2 fluxes. NOAA has made improvements to a design originally developed by MBARI, and previously worked with Battelle to manufacture the MApCO2 system¹. The latest ASVCO2

### 2 sensor is designed to measure the partial pressure CO2 concentration of sea

water and surrounding air. From these measurements an evaluation of the temporal variability in air-sea CO2 fluxes can be used to assist in identifying the associated air-sea exchange mechanisms. This ASVCO2 sensor is a modification of the original pCO2 system developed by PMEL and Battelle in 2009. By eliminating non-pCO2 capabilities (e.g., SSTC, Iridium, etc.), this sensor is a dependant sensor which requires other data-logging and telemetry systems. Additionally to calculate pCO2 and fCO2, sea surface temperature and salinity measurements are required.

# Specifications

Power Requirements

Voltage Requirement | 6 - 18V DC
Average Run Current per sample (~18.167 minutes)* | 90mA
Average Run Current (1 sample/hour)* | 27mA
Peak Current per sample* | 685mA
Sleep Current * ** Communication | 4mA
Digital Format - Command | RS-232

1 Sutton, A.J., C.L. Sabine, S. Maenner-Jones, N. Lawrence-Slavas, C. Meinig, R.A. Feely, J.T. Mathis, S. Musielewicz, R. Bott, P.D. McLain, J. Fought, and A. Kozyr (2014): A high-frequency atmospheric and seawater pCO2 data set from 14 open ocean sites using a moored autonomous system. Earth Sys. Sci. Data, 6, 353–366, doi: 10.5194/essd-6-353-201. 2 Sabine, C., A.J. Sutton, K. McCabe, N. Lawrence-Slavas, S.R. Alin, R.A. Feely, R. Jenkins, S. Maenner, C.

Meinig, J. Thomas, E. van Ooijen, A. Passmore, and B. Tilbrook (2020): Evaluation of a new carbon dioxide system for autonomous surface vehicles. J. Atmos. Oceanic Tech., 37(8), 1305–1317, doi: 10.1175/JTECH-D-20-0010.1.

3

Digital Format - Console Measurement | USB (Virtual Serial Port)
Average Sample Run Time | 18 minutes, 30 seconds
Sampling Frequency | 2 hertz
* Running at 12V DC nominal
** Sleep current is not optimized, so unit should be shut off between runs.

# Operational Theory

The ASVCO2 Sensor has six states of operation during a standard sample. The following diagram depicts the states in order of operation with an attempt at graphically indicating the lengths of each state. The config and rest states are overly exaggerated to fit the text within the blocks, while the equilibrate state is underexaggerated due to size restrictions.
Note: In the state diagrams following, any words in red indicate variable times that can be set by the user. Some of these variables are used in other states (i.e., warmup, pumpon, etc.), and can affect the operation of the system significantly.

## Full Run

## Config State

The config state configures the sensor for the requested run. When a run is requested, all sensor variables are locked. Run Start

Initialize
Subsystems
(6 seconds)

Licor Warmup
(30 seconds typical)

Licor Configure
(2 seconds) Licor Power ON | Licor Configure

4

## Zero Position (ZP) State

During the Zero state, the flow control module is commanded to run atmospheric air through the dryer and the soda lime, creating an air sample devoid of CO2 with extremely reduced relative humidity. This sample is used to provide a reference setting to the Li-COR NDIR CO2 sensor. Zero, Pump ON

Zero Pump ON
(30 seconds typical)

Sample
(30 seconds typical)

Zero Pump OFF*
(15 seconds typical)

Sample

(30 seconds typical) Zero Calibration (15 seconds typical)

Sample (Post Cal)

(30 seconds typical) Sample Start | Pump Off | Sample Start | Zero Commanded | Sample Start

## Span Position (SP) State

The Span State is used to calibrate the Li-COR NDIR CO2 sensor with a known CO2 concentration sample. The flow control unit is commanded to route the bottled CO2 standard through the dryer and into the Li-COR Span, Flow OPEN

Span FLOW ON
(30 seconds typical)

Sample
(30 seconds typical)

Span Pump OFF*
(15 seconds typical)

Sample
(30 seconds typical)

Span Calibration
(15 seconds typical)

Sample (Post Cal)

(30 seconds typical) Sample Start | Flow CLOSED | Sample Start | Span Commanded | Sample Start

## Equil Position (EP) State

The equil (equilibration) state is where the seawater CO2 concentration is measured. A clean air sample (from the atmosphere) is bubbled in the equilibrator to equalize the partial pressures of the water sample and the trapped air. This is typically the longest state in the process as the equilibration process requires a significant amount of time. Licor Power OFF Equil, Pump ON

Equilibrate Pump ON
(570 seconds typically)

Sample
(30 seconds typical)

EQUIL Pump OFF*
(15 seconds typical)

Sample
(30 seconds typical) Sample Start | Pump Off | Sample Start

Warmup
(30 seconds typical) Licor Power ON

5

## Air Position (AP) State

The air state is where the atmospheric CO2 is measured. The flow controller routes the atmospheric air through the dryer and into the Li-COR for measurement. After the atmospheric CO2 is measured, the sensor recalibrates the O2 sensor.

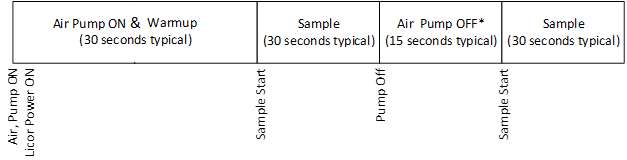
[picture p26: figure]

## Rest State

At the conclusion of the sample, the sensor is put into the rest state. The flow controller closes all valve entries from exterior to prevent water damage to the sensing system.

Results Rest State | Low Power Mode

## Pump Off (Substate)

In the previous states, a sub-state labeled “Pump OFF*” was shown. The following timing diagram shows the components of the pump-off sub-state:

Delay
(~3 seconds)

Pressure
Equilization
(2 seconds) Vent CLOSED

Vent
(10 seconds typical) Vent OPEN

6

## Purge State (Optional)

The purge state is added to a run by running the “TSP” or “TSQP” commands. This state is used to help remove any moisture buildup in the tubing. PURGE TIME and VENT TIME are variable. Following the purge, the system is put into rest state.

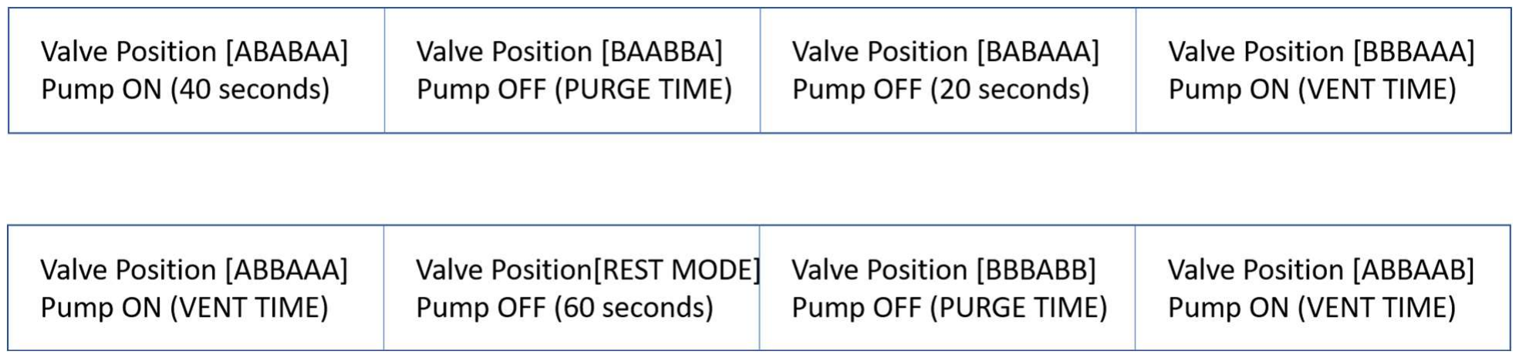
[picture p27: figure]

# User Interface(s)

## I. Physical Interface - Bulkhead Connectors

The ASVCO2 Gen 2 sensor has a single 8-pin Subconn MCBH8M bulkhead connector used for all power and communications. See Section II. for communication setup.

Pin # | Function | Limits/Notes
1 | GND | System Ground
2 | Tx | RS232 Transmit (to user)
3 | Rx | RS232 Receive (from user)
4 | +V | Input Voltage (6-18VDC)
5 | +5VDC | USB Power (+5VDC)
6 | D- | USB Data (Negative)
7 | D+ | USB Data (Positive)
8 | GND | USB Ground

Subconn MCBH2M Bulkhead Connector Pins

Mating parts for bulkhead connector:

7

Part Number | Qty | Description
MCIL8F | 1 | Mating Cable
MCDLS Snap Ring | 1 | Locking Sleeve Snap Ring
MCDLS-F | 1 | Locking Sleeve

## II. Physical Interface - PCB

The ASVCO2 Gen2 sensor has two interfaces, command port (RS232) and console port (USB), used to connect to users and control systems.

## Command Port

The command port (Connector receptacle J1 on the PCB) is a combination power and serial port which is intended for M2M communications, i.e. control by autonomous vehicle or buoy controller.

Pin # | Function | Limits/Notes
1 | GND | System Ground
2 | Tx | RS232 Transmit (to user)
3 | Rx | RS232 Receive (from user)
4 | +V | Input Voltage (6-18VDC)

Command Port Connector Pins

RS232 Property | Setting
Baud Rate | 115,200
Data bits | 8
Parity | None
Stop bits | 1
Flow Control | None
Termination Character(s) | CR & LF (\r\n)

Command Port Serial Connection Settings

8

## Console Port

The Console port (USB) was designed for system configuration and testing during the manufacturing phase. A USB-to-Serial integrate circuit allows the ASVCO2 to show up as a Virtual COM port on a PC.

USB Property | Setting
Baud Rate | 115,200
Data bits | 8
Parity | None
Stop bits | 1
Flow Control | None
Termination Character(s) | CR & LF (\r\n)

Console Port Serial Connection Settings

9

## III. Hotkeys (Console Port Only (USB))

When the system is woken up (by sending any character) from Low Power Mode (LPM) it enters a wait state where it is looking for a user command for the next 5 seconds, or it will go back to the LPM. The following commands are available during this wait state:

Command | Action | Definition
? R | Show Help Menu Start Sample Run | Show List of Hotkey Commands Start a full cycle pCO2 measurement run with normal sample periods
u O | Start sample, quick test Calibrate O2 Sensor | Start a quick pCO2 measurement test with fast sample periods Pump atmospheric air through O2 sensor for 30 seconds and calibrate ADC for 20.947 %O2.
T t | Console Terminal Mode Get Time | Enter the console terminal for full-featured configuration menu. Get the current RTC time.
S | Current Sampling Mode Current Sampling Schedule | Which Mode the system is currently in (Fast, Normal or Deploy) (Not currently implemented) s Show the current scheduler functions with start times (Not currently implemented)
d | Get System Settings | Return a list of configurable system settings.
A | Air Mode (Purge) | Runs Air Mode to purge Licor of possible condensation
q | Return to Sleep Mode | Exit program and return to LPM.

## IV. The Terminal: Console & Command Port Commands

The Terminal can be entered through both the Console Port (USB) or the Command Port (RS232). To enter from the Console port, a wakeup key (any key) followed by a “T” will bring up the terminal. From the Command port, a wakeup key (any key) will automatically enter the Terminal.
Once the terminal is entered, a ‘>’ will be shown. If the sensor has previously been assigned a serial number, the serial number will precede the ‘>’.

10

Both ports will return to sleep after a period of inactivity. For the both console (USB) and command(RS232), this is approximately 60 seconds.

The following commands are available from the Terminal: System Commands (Read Only):

Command | Action | Definition
? Ctrl-C (ASCII 0x03) | Show Help Menu Reset System | Show List of Hotkey Commands Restart System
q | Exit Terminal Mode | Exit Terminal and return to Low Power Mode
report | Get System Settings Show Firmware Version | Return a list of configurable system settings. ver Show the firmware version running on this device
i2cfail startup | Show the number of I2C failures Show the number of system startups | Show the number of I2C failure/restarts since power-up Show the number of systems startups since the device was programmed

11

## System Commands

Command | Action | Definition
serial serial= XXXXXXXX | Show Serial Number Set the serial number | Show the device serial number Set the device serial number [18 characters max] [For PMEL Devices, this should be ASVCO2xxxx. Xxx can be 12 char long]
sreset time time= yy mm dd hh mm ss Baud baud= X | Software Reset Show current time Set current time Show Serial Baudrate Set Serial Baudrate | Reset the device by using the software reset (Quick response) Show the current RTC time (ISO-8601 format) Sets the current datetime (yy mm dd hh mm ss) Shows the current buadrate setting Set the serial port baudrate (2400, 4800, 9600, 19200, 28800, 38400, 57600, 115200)

## TELOS Compliant Commands

Command | Action | Definition
cshow gps | Show COM Data GPS Data | Report dummy TELOS COM data Always reports -2 for PCO2 Sensor
time time= idata sdata | Sensor Date & Time Set Sensor Date & Time Iridium Data Sample Data | Time in format (yy mm dd hh mm ss) Time in format(yy mm dd hh mm ss) Show the iridium (real-time) data Show the high frequency data set

12

who | Serial Number | Show the system serial number

## pCO2 Configuration Commands

Command | Action | Definition
span span= XXXXX.XX | Show the Span Gas Concentration Set the span gas concentration | Show the span gas concentration (μmol mol⁻¹) stored in memory Set the span gas concentration in μmol mol⁻¹. (Default: 300umol mol⁻¹)
span2 | Show the Secondary Span Gas Concentration | Show the Secondary Span gas concentration (μmol mol⁻¹) stored in memory
span2= XXXXX.XX | Set the Secondary Span gas concentration Show the Span Pressure | Set the secondary span gas concentration in μmol mol⁻¹. spandiff
spandiff= XXX.XX | Difference (kPa) Set the span pressure difference | Show the minimum pressure difference between SPON and SPOFF that allows for automatic span calibration during a run. If this pressure difference is not exceeded, the calibration (span) gas cylinder is likely empty.. Set the pressure difference that determines if the system span calibrates during a run. In kPa. [default= 0.4kPa]
equil equil= SSS | Show equilibration pump time Set the equilibration pump time | Show the length of the equilibration pump time in seconds Set the length of the equilibration pump time in seconds
warmup warmup= SSS | Show the LICOR warmup time Set the length of the LICOR warmup | Show the length of the LICOR warmup time in seconds Set the LICOR warmup time length in seconds
pumpon | Show the pump on time | Show the length of pump on time during a sample cycle in

13

pumpon= SSS | Set the pump on time | seconds. Pump on time also controls the flush time for the span gas. CO2 is not sampled during the pump on time. Set the length of pump on time during a sample in seconds
pumpoff pumpoff= SSS | Show the pump off time Set the pump off time | Show the length of pump off time during a sample in seconds. Pump off times encompasses: 1) a pressure settle period (set as a constant in the firmware of 3 sec), 2) user defined vent period (see below), 3) followed by 2nd pressure settle period (length of this period is pumpoff time minus (vent time + 3 secs) Set the length of pump off time during a sample in seconds
sampleco2 sampleco2= SSS | Show the data sample length time Set the data sample length time | Show the length of time the sample is collected during a sample in seconds in its current state. Set the length of time the sample is collected during a sample in seconds in its current state.
vent vent= SSS | Show the vent delay time Set the vent delay time | Show the length of delay time between vent open/close events in seconds Set the length of delay time between vent open/close events in seconds
heater heater= X | Show the LICOR heater state Set the LICOR heater state | Show the current ON/OFF state of the LICOR Heater Set the LICOR heater state (0=OFF, 1=ON). Heater default state is OFF since the heater is not used in the field.

14

## Logging Commands

Command | Action | Definition
ts | Take sample | Start a sample run immediately
tsq | Take sample – Quiet Mode | Start a sample run immediate: only show only display start and stop of run on Command port. No other messaging. Can send an “sdata” or “idata” command after the run is complete. Start indicated by “Starting Sample - Quiet Mode" Complete indicated by "Sample Complete"
tsp | Take sample w/Purge | Start a sample run immediately and run the purge routine when complete.
tspq | Take sample w/Purge – Quiet Mode | Same as “tsq” with the purge routine run prior to completion.

## Test Mode Commands

Command | Action | Definition
test stream | Enter TEST mode Stream Data | Put system in TEST mode Stream system data (any key to exit)
norm | Enter Normal Mode | Return from TEST mode into Normal mode

## Flow Control Module Commands - Requires System in TEST MODE

Command | Action | Definition
flowon | Turn Flow Control Module
ON
| | Set relay to apply power to the Flow Control Module(MUST BE IN TEST

MODE)

15

flowoff | Turn Flow Control Module OFF | Clear the relay to cut power to the Flow Control Module(MUST BE IN TEST MODE)
fpulse | Flow Control Pulse Length | Sets the flow control pulse length (10-100ms)
fcurrent | Flow Control Current Setting | Sets the flow control current setting (0-7)
flowpass | Flow Control Passthrough | Allows direct UART access to the Flow Controller in the field
fpurge | Flow Control Purge | Run the purge routine

## Valve Setting Commands - Requires System in TEST MODE

Command | Action | Definition
tpos | Start data streaming | Starts in REST mode, use following keys to cycle between modes (MUST BE IN TEST MODE)
q p | Exit Toggle Pump | Exit TPOS mode Toggles Pump OFF/ON in positions that utilize the pump
a | AIR Positions EQUILIBRATE Positions | Cycles through AIR Positions (APON, APOFF). e Cycles through EQUIL
| REST position. ZERO Positions SPAN positions | Positions (EPON, EPOFF). r Sets REST position. z Cycles through ZERO positions (ZPON, ZPOFF, Cycles though SPAN positions ZPPCAL). s
0 | Perform ZERO Cal | (SPON, SPOFF, SPPCAL). Send the Licor a re-zero command
1 | Perform SPAN Cal | Runs the LI-COR SPAN

16

Calibration

### 2 Performs SECONDARY SPAN

Cal

Runs the LI-COR SECONDARY
SPAN Calibration

17

## Licor Testing Commands – Requires System in TEST MODE

Command | Action | Definition
licoron licoroff | Turn LICOR ON Turn LICOR OFF | Set relay to apply power to LICOR (MUST BE IN TEST MODE) Clear relay to remove power to LICOR (MUST BE IN TEST MODE)
licorcfg | Configure LICOR | Run LICOR initial configuration (MUST BE IN TEST MODE)
likzero | READ CO2KZERO | Read co2kzero value from LI-830
likzero= n.nnnnnnnn | SET CO2KZERO | Set co2kzero value on LI-830
likspan | READ CO2KSPAN | Read co2kspan value from LI-830
likspan= n.nnnnnnnn | SET CO2KSPAN | Set co2kspan value on LI-830
likspan2 | READ CO2KSPAN2 (Secondary Span) | Read co2kspan2 (Secondary Span) value from LI-830
likspan2= n.nnnnnnnn | SET CO2KSPAN2 | Set co2kspan2 value on LI-830
lisample heateron | Sample the LICOR Turn LICOR heater ON | Read a LICOR sample (MUST BE IN TEST MODE) (Not currently implemented) Turn LICOR Heater on (requires high current input) (MUST BE IN TEST MODE)
heateroff lipass liver | Turn LICOR heater OFF LICOR COMS passthrough LICOR firmware version | Turn LICOR heater off (MUST BE IN TEST MODE) Create a tunnel to the LICOR to directly talk to the sensor through the terminal (MUST BE IN TEST MODE) Read the LICOR firmware version number.

18

## Oxygen Sensor Commands - Requires System in TEST MODE

Command | Action | Definition
O2 O2volt | Read O2 Sensor Read O2 Sensor Voltage | Read the O2 Sensor value in %. (MUST BE IN TEST MODE) Read the O2 sensor voltage in volts. (MUST BE IN TEST MODE)
o2cal | Calibrate O2 Sensor Turn the analog port ON | Run the O2 Calibration Routine. (MUST BE IN TEST MODE) anaon Apply power to the analog voltage reference. (MUST BE IN TEST MODE)
anaoff | Turn the analog port OFF | Clear power to the analog voltage reference. (MUST BE IN TEST MODE)

## Relative Humidity Sensor Commands - Requires System in TEST MODE

Command | Action | Definition
rh | Read the RH sensor | Read the relative humidity sensor in %RH. (MUST BE IN TEST MODE)

19

## Real-time Clock Commands

Command | Action | Definition
rtccal | Set RTC Calibration | Turns on the 32kHz signal on the RTC output used for calibrating the crystal. System then waits for next field to be entered:
XXXXX.XX | Program the RTC | Enter the actual frequency of the crystal measured to auto- calculate the RTC offset for most accurate timing
treg | RTC Register Value | Shows hex values of RTC registers (for debugging purpose)
tcon | Charge RTC Cap | Applies voltage to the RTC SuperCap
tcoff | Stop Charge RTC Cap | Turns RTC SuperCap off
tcal | Autocal RTC RC Osc | Autocalibrates the RTC osciallator

20

## Manufacturer Configuration Commands

To access these commands you need to first unlock them using the “mconfig” command, you then have USB= 60sec & RS232 = 10sec to enter the commands before your access expires and you need to reenter the “mconfig” command.

## These commands are used for NetCDF generation

Command | Action | Definition
mconfig= PMEL | Allow Access to Manufacture Commands | Simple password protection for remainder of Manufacturer Configuration Commands (use “mconfig= PMEL” to see the
values) ssct | Read
| secondaryspan_calibrated_temperature | Show the Licor temp at the time that the Secondary Span Coefficient was set.
ssct= x.xxx | Write secondaryspan_calibrated_temperature | Record the Licor temp at the time that the Secondary Span
Coefficient was set. sscsc | Read
| secondaryspan_calibrated_spanconcentra tion | Show the concentration of the span gas used during the Secondary Span calibration routine. (This is the concentration for the mid-level
span1 gas). sscsc= x.xx | Write
| secondaryspan_calibrated_spanconcentra tion | Record the concentration of the span gas used during the Secondary Span calibration routine. (This is the concentration for the mid-level span1 gas).
lssc | Read last_secondaryspan_calibration | Show the date of the last secondary span calibration.
lssc= YYYY-MM- DDThh:mm:ssZ | Write last_secondaryspan_calibration | Record the datetime of the secondaryspan calibration.
lsstds | Read last_secondaryspan_temperaturedependa ntslope | Show the date of the last Secondary Span temperature dependant slope determination.
lsstds= YYYY- MM- DDThh:mm:ssZ | Write last_secondaryspan_temperaturedependa ntslope | Record the date of the last Secondary Span temperature dependant slope

21

determination.

sstds Read secondaryspan_temperaturedependantsl ope

Show the secondary span’s
temperature dependant slope, which is defined as the Licor’s linear fit between the
Secondary Span Coefficient and detector temperature
between 0 and 40 deg C.
presented as change in
secondary span coefficient value per deg. C. This slope may be applied during the post processing of the data to
improve measurement
accuracy.

sstds=

x.xxxxxxxx | Write secondaryspan_temperaturedependantsl ope | Record the secondary span’s temperature dependant slope, which is defined as the Licor’s linear fit between the Secondary Span Coefficient and detector temperature between 0 and 40 deg C. presented as change in secondary span coefficient value per deg. C. This slope may be applied during the post processing of the data to improve measurement accuracy.
sstdsf | Read secondaryspan_temperaturedependantsl opefit | Show the R^2 linear fit of the secondary span’s temperature dependency determination.
sstdsf= x.xxx | Write secondaryspan_temperaturedependantsl opefit | Record the R^2 linear fit of the secondary span’s temperature dependency determination.
sscrh | Read secondaryspan_calibrated_RH | Show the RH of the gas stream in the licor when the Secondary Span Coefficient was set.
sscrh= x.xx | Write secondaryspan_calibrated_RH | Record the RH of the gas stream in the licor when the Secondary Span Coefficient
was set. sscssn | Read | Show the serial number of the

22

secondaryspan_calibrated_spanserialnum ber

span gas (S0) bottle used while setting the secondary span. sscssn= Write

secondaryspan_calibrated_spanserialnum ber

Record the serial number of the span gas (S0) bottle used while setting the secondary span. ssconc Read

ASVCO2_secondaryspan_concentration

Show the concentration of the secondary span gas used to set the Secondary Span
Coefficient. This will be the highest concentration gas. An example might be 2500 μmol mol⁻¹. sssn Read

ASVCO2_secondaryspan_serialnumber

Read the serial number of the secondary span gas (S1) bottle used while setting the
secondary span. sssn= Write

ASVCO2_secondaryspan_serialnumber

Record the serial number of the secondary span gas (S1) bottle used while setting the
secondary span. ssn | Read ASVCO2_span_serialnumber | Read the serial number of the

span gas (S0) bottle used in the ASVCO2 system

ssn= | Write ASVCO2_span_serialnumber | Record the serial number of the span gas (S0) bottle used in the ASVCO2 system
avalid | Read last_ASVCO2_validation | Show the last time that the ASVCO2 system was validated against a suite of WMO certified gas standards.
avalid= YYYY- MM- DDThh:mm:ssZ | Write last_ASVCO2_validation | Record the last time that the ASVCO2 system was validated against a suite of WMO certified gas standards.
pbias | Read pressure_bias | Show the bias of the Licor pressure sensor. Obtained when the ASVCO2 system is open to the atmosphere (APON state) and its pressure is compared to a certified barometer. This bias is applied during the post processing process to

23

determine the partial pressure of CO2.

pbias= x.xx | Write pressure_bias | Record the bias of the Licor pressure sensor. Obtained when the ASVCO2 system is open to the atmosphere (APON state) and its pressure is compared to a certified barometer. This bias is applied during the post processing process to determine the partial pressure of CO2.
lpbm | Read last_pressure_bias_measured | Show the date of the most recent pressure bias determination.
lpbm= YYYY- MM- DDThh:mm:ssZ | Write last_pressure_bias_measured | Record the date of the most recent pressure bias determination.
atrhs | Read ASVCO2_ATRH_serial | Show the serial number of the
internal ASVCO2 AT/ RH sensor. atrhs= ssssssss | Write ASVCO2_ATRH_serial

(Currently User Disabled)

Placing the system in
[TESTMODE] will save the
attached ATRH sensor’s serial number
o2s | Read ASVCO2_O2_serial | Show the serial number of the
internal ASVCO2 oxygen sensor. o2s= sssssss | Write ASVCO2_O2_serial | Record the serial number of
the internal ASVCO2 oxygen sensor. mfr | Read ASVCO2_manufacturer | Show the manufacturer of the

ASVCO2 system.

mfr= ssssssssssssssss | Write ASVCO2_manufacturer | Record the manufacturer of the ASVCO2 system.

24

## DATA Format

All data reported during a run is returned with the “Data:” tag and has the following form:

DATA: State,TS,SN,CO2(ppm),Li_temp,Li_pres,Li_RawSample,Li_RawReference,RH(%),RH_T(C),O2(%) Where:
State – Current pCO2 sample mode
TS – Timestamp (in ISO-8601 format, YYYY-MM-DDTHH:MM:SSZ)
SN – Serial Number of pCO2 sensor
CO2(ppm) – CO2 concentration in parts per million (ppm) Li_temp(C) – LICOR CO2 sensor chamber temperature in degrees C Li_pres(kPa) – LICOR CO2 sensor chamber pressure in kilopascals Li_RawSample – LICOR CO2 sensor raw data measurements Li_RawReference – LICOR CO2 reference data
RH(%) – Relative humidity percentage
RH_T(C) – Relative Humidity sensor temperature measurement in degrees C O2(%) – Percentage Oxygen measured

Example:

DATA: APOFF , 2021-03-29T23:25:29.5Z, ASV1007, 438.470, 21.157, 101.506, 5488897, 5920678, 43.409, 20.468, 20.907

## STATS Format

All statistical data (mean and standard deviation of measurements) reported during a run is
returned with the “STATS:” tag and has the following form: STATS: State,SN,Timestamp,Li_Temp_ave(C),Li_Temp_sd,Li_Pres_ave(kPa),Li_Pres_sd,CO2_ave(PPM),CO2_SD,O2_ave(%),O2_SD,RH

_ave(%),RH_sd,RH_T_ave(C),Rh_T_sd,Li_RawSample_ave,Li_RawSample_sd,Li_RawDetector_ave,Li_RawReference_sd Where:

State – Current pCO2 sample mode
SN – Serial Number of pCO2 sensor
TS – Timestamp (in ISO-8601 format, YYYY-MM-DDTHH:MM:SSZ) Li_Temp_ave(C) – Licor mean temperature (degrees C) Li_Temp_sd – Licor temperature standard deviation (degrees C) Li_Pres_ave(kPa) – Licor mean pressure (kPa)
Li_Pres_sd – Licor pressure standard deviation (kPa) CO2_ave(PPM) – Licor mean CO2 (ppm)
CO2_SD – Licor CO2 standard deviation (ppm) O2_ave(%) –Mean Oxygen (%O2)
O2_SD –Oxygen standard deviation (%O2)
RH_ave(%) – Mean Relative Humidity (%RH)
RH_sd – Relative Humidity Standard Deviation (%RH)
RH_T_ave(C) - Mean Relative Humidity Temperature (degrees C) Rh_T_sd - Relative Humidity Temperature standard deviation(degrees C)

25

Li_RawSample_ave – Licor Mean Raw1 reading Li_RawSample_sd – Licor Raw1 reading standard deviation Li_RawDetector_ave – Licor Mean Raw2 reading
Li_RawReference_sd - Licor Raw2 reading standard deviation
Example:

STATS: SPON , ASV1007, 2021-03-29T23:10:50Z, 20.573, 0.021, 102.904, 0.006, 503.835, 0.605, 20.984, 0.051, 43.421, 0.051, 20.194, 0.011, 5422553, 601, 5925315, 457

## LOG Format (only available in Console/USB)

All mode and engineering data are returned with the “LOG:” tag. The messages are designed to be human-readable and have no specific format. They are prepended with the timestamp for diagnostic purposes.
Example:
LOG: 2019-05-22T11:24:39Z, Start ZERO PUMP ON
LOG: 2019-05-22T11:24:40Z, Start Pump 30 seconds LOG: 2019-05-22T11:25:10Z, Sample - Real Time
LOG: 2019-05-22T11:25:11Z, Sample Data 30 seconds

## DRY Format

At the end of each sample, the dry Atmospheric and Water CO2 measurements are computed and displayed to the user using the “DRY:” tag and the following format. NOTE: If spandiff is not met, the DRY field will not be displayed.
DRY: TS, SW_xCO2(dry), Atm_xCO2(dry)<CR><LF>
DRY: YYYY-MM-DDTHH:MM:SSZ, xxx.xxx, yyy.yyy<CR><LF>

Where:
YYYY - Four-digit year
MM - Two-digit month
DD - Two-digit day
HH - Two-digit hour (24-hour clock)
MM - Two-digit minute
SS - Two-digit seconds
xxx.xxx - Floating point Seawater pCO2 value (ppm) yyy.yyy - Floating point Atmospheric air pCO2 value (ppm)

Example:
DRY: TS, SW_xCO2(dry), Atm_xCO2(dry)
DRY: 2019-05-21T15:13:31Z, 198.01, 253.79

26

## REPORT Format

Sending the hotkey command “d” or the console command “report” returns the system variables. The format is as follows:
ASVCO2v2<CR><LF
serial= CCCCCCCCCCCCCCCCCCCC<CR><LF>
ver= CCCCCCCCCCCCCCCCCCCC<CR><LF> startup= UUUUUUUUUUUUUU<CR><LF> gps= -2<CR><LF>
time= YYYY-MM-DDTHH-MM-SSZ<CR><LF> span= FFFF.FFFF<CR><LF>
spandiff= F.FFFF<CR><LF>
equil= UUUU<CR><LF>
warmup= UUUU<CR><LF>
pumpon= UUUU<CR><LF>
pumpoff = UUUU<CR><LF>
sampleco2= UUUU<CR><LF>
vent= UUUU<CR><LF>
heater= U<CR><LF>
sample= UUUU<CR><LF>
LI_ser = CCC-CCCC<CR><LF>
LI_ver = C.C.C<CR><LF>
LI_ccva1= F.FFFFF<CR><LF>
LI_ccva2= F.FFFFF<CR><LF>
LI_ccva3= F.FFFFF<CR><LF>
LI_ccva4= F.FFFFF<CR><LF>
runtime-= HH:MM:SS<CR><LF> secondaryspan_calibrated_temperature= F.FFF<CR><LF> secondaryspan_calibrated_spanconcentration= F.FF<CR><LF> last_secondaryspan_calibration= YYYY-MM-DDTHH:MM:SSZ<CR><LF> last_secondaryspan_temperaturedependantslope= YYYY-MM-DDTHH:MM:SSZ<CR><LF> secondaryspan_temperaturedependantslope= F.FFFFFFFF<CR><LF> secondaryspan_temperaturedependantslopefit= F.FFF<CR><LF> secondaryspan_calibrated_rh= F.FF<CR><LF> secondaryspan_calibrated_spanserialnumber= CCCCCCCCCCCCCCCCCCCCCCCC<CR><LF> ASVCO2_secondaryspan_concentration= FFFF.FF<CR><LF> ASVCO2_secondaryspan_serialnumber= CCCCCCCCCCCCCCCCCCCCCCCC<CR><LF> ASVCO2_span_serialnumber= CCCCCCCCCCCCCCCCCCCCCCCC<CR><LF> last_ASVCO2_validation= YYYY-MM-DDTHH-MM-SSZ<CR><LF> pressure_bias= F.F<CR><LF>
last_pressure_bias_measured= YYYY-MM-DDTHH-MM-SSZ<CR><LF> ASVCO2_ATRH_serial = CCCCCCCCCCCCCCCCCCCCCCCC<CR><LF> ASVCO2_O2_serial= CCCCCCCCCCCCCCCCCCCCCCCC<CR><LF> ASVCO2_manufacturer= NOAA/PMEL

Where:

27

ASVCO2v2 is the sensor version
serial= The sensor serial number (up to 20 characters) ver= Firmware Version Number (up to 20 characters)

startup= Number of time system has been started (ASCII represented unsigned integer) gps= -2 (Constant used in PMEL systems)
time= ISO-8601 Timestamp format. UTC Time.
span= Span CO2 Concentration (ppm, ASCII represented floating point)
equil= Equilibration time (seconds, ASCII represented unsigned integer) pumpon= Pump ON time (seconds, ASCII represented unsigned integer) pumpoff= Pump OFF time (seconds, ASCII represented unsigned integer) sampleco2= CO2 sample time (seconds, ASCII represented unsigned integer) vent= Sensor vent time (seconds, ASCII represented unsigned integer) heater= Heater Set state (0=OFF, 1=ON)
sample= Licor Sampling Frequency (Hz, ASCII represented unsigned int) LI_ser = Licor Serial Number
LI_ver = Licor Firmware Version
LI_ccva1 = Licor CO2 calibration value #1
LI_ccva1 = Licor CO2 calibration value #2
LI_ccva1 = Licor CO2 calibration value #3
LI_ccva1 = Licor CO2 calibration value #4
runtime= Estimated time for a full sample (seconds)
secondaryspan_calibrated_temperature= Temperature recorded during secondary cal (degC) secondaryspan_calibrated_spanconcentration= CO2 Concentration used at secondary cal (ppm) last_secondaryspan_calibration= Datetime of secondary cal last_secondaryspan_temperaturedependantslope= Datetime of secondary span fit calc secondaryspan_temperaturedependantslope= Slope of secondary cal temperature fit secondaryspan_temperaturedependantslopefit= Offset of secondary cal temperature fit secondaryspan_calibrated_rh= RH at secondary cal (%RH) secondaryspan_calibrated_spanserialnumber= RH sensor serial number used for secondary cal ASVCO2_secondaryspan_concentration= Secondary span conc used for calculation co2 (ppm) ASVCO2_secondaryspan_serialnumber= Serial number of secondary span gas ASVCO2_span_serialnumber= Serial number of span gas onboard sensor last_ASVCO2_validation= Datetime of last validation
pressure_bias= Pressure bias of calculation
last_pressure_bias_measured= Datetime of last pressure bias measurement ASVCO2_ATRH_serial = ATRH used Serial Number
ASVCO2_O2_serial= Onboard O2 sensor Serial Number ASVCO2_manufacturer= NOAA/PMEL

Note:
LI_ser, LI_ver, LI_ccva1, LI_ccva2 LI_ccva3, LI_ccva4, are all directly read from the Licor on the first Licor config/power-up.

28

Example:
ASVCO2v2
serial= ASV2001
ver= v1.8-12-g001ac12
startup= 2
gps= -2
time= 2000-01-06T18:29:15Z span= 500.000000
spandiff= 0.400000
equil= 600
warmup= 30
pumpon= 30
pumpoff= 15
sampleco2= 30
vent= 10
heater= 0
sample= 2
LI_ser= CGA-5180
LI_ver= 1.0.4
LI_ccva1= 0.10000
LI_ccva2= 1.80000
LI_ccva3= 0.45000
LI_ccva4= 18.00000
runtime= 00:18:30
secondaryspan_calibrated_temperature= 27.300 secondaryspan_calibrated_spanconcentration= 2102.80 last_secondaryspan_calibration= 2021-08-04T09:32:23Z last_secondaryspan_temperaturedependantslope= 2021-08-01T17:11:32Z secondaryspan_temperaturedependantslope= 9.10000100 secondaryspan_temperaturedependantslopefit= -3.810 secondaryspan_calibrated_rh= 47.20 secondaryspan_calibrated_spanserialnumber= CO2SP1a800 ASVCO2_secondaryspan_concentration= 2101.32 ASVCO2_secondaryspan_serialnumber= CO2SP2a210132 ASVCO2_span_serialnumber= CO2SP2a05119 last_ASVCO2_validation=
pressure_bias= 2.3
last_pressure_bias_measured= 2021-08-01T16:43:11Z ASVCO2_ATRH_serial = RH218139aa80 ASVCO2_O2_serial = T23Aca8ad
ASVCO2_manufacturer= PMEL/EDD

## SLEEP Format

SLEEP indicates the microcontroller is in low-power “sleep” mode. This is the only mode where power-off is considered safe.

29

## COEFF Format

During the run, the ASVCO2 sensor will report the coefficients generated by the Licor and the O2 sensors in both the Console and Command ports. These coefficients are needed during the data QC process and are important for the interpretation of raw data, the ability to re-calculate xCO2 from raw counts, and should be stored with the archived data. The format of the string for the Licor is:

The coefficients are returned as follows
COEFF: Licor -
COEFF: CO2LastZero: DD MMM YYYY
COEFF: CO2kzero: f.ffffffffE+dd COEFF: CO2LastSpan: DD MM YYYY COEFF: CO2LastSpan2: YYYY-MM-DD COEFF: CO2kspan: f.ffffffffE+dd COEFF: CO2kspan2: f.ffffffffE+dd COEFF: O2 -
COEFF: co2cal= f.fff
Where:
f.fff is a single precision float number
f.fffffffE+dd is a double precision number in exponential format DD is the two digit day
MM is the two digit month
YYYY is the four digit year
Example:
COEFF: Licor -
COEFF: CO2LastZero: 13 APR 2021 COEFF: CO2kzero: 1.20267850E+00 COEFF: CO2LastSpan: 06 APR 2021 COEFF: CO2LastSpan2: 2020-11-10 COEFF: CO2kspan: 5.45022040E+03 COEFF: CO2kspan2: 1.00100000E+02
COEFF: O2 -
COEFF: o2cal= 3.219
The ASVCO2’s xCO2 values during the different states within a measurement run are calculated using the coefficients as detailed below. “Old” designates the coefficients stored on the licor from the last time the licor was calibrated, this will be the previous measurement run unless the system experienced a calibration error flag. The secondary span is calibrated and set in the lab before each instrument deployment.

ZPON- old zero, old span, lab secondary span
ZPON - old zero, old span , lab secondary span
ZPPOFF - new zero, old span , lab secondary span SPON - new zero, old span , lab secondary span SPOFF - new zero, old span , lab secondary span SPPCAL- new zero, new span , lab secondary span

30

EPON - new zero, new span , lab secondary span EPOFF - new zero, new span , lab secondary span APON - new zero, new span , lab secondary span
APOFF - new zero, new span , lab secondary span

## V. TELOS/Post-Sensing data

After a “ts” or “tsq” command is sent and the sensor completes a run, the sample data and the TELOS compliant “iridium” data are stored for future use. Only the previous run is stored; once another “ts” or “tsq” is commanded the memory is cleared.

## “sdata” Format

The high frequency data (2Hz) is collected in memory during the run (ts/tsq) so that the data can be retrieved after the run using the “sdata” command. “ts” or “tsq” must be run before this data is valid. The data has the following format:

"State,TS,CO2(ppm),Li_Temp(C),Li_Pres(kPa),Li_Raw,Li_Ref,RH(%),RH_T(C),O2(%),xCO2(dry),xCO2(wet), co2kzero, co2kspan, co2kspan2, errors"
Where:
State – Current pCO2 sample mode
TS – Timestamp (Integer values in 0.5second increments) CO2(ppm) – CO2 concentration in parts per million (ppm) Li_Temp(C) – LICOR CO2 sensor chamber temperature in degrees C Li_Pres(kPa) – LICOR CO2 sensor chamber pressure in kilopascals Li_Raw – LICOR CO2 sensor raw data measurements
Li_Reference – LICOR CO2 reference data
RH(%) – Relative humidity percentage
RH_T(C) – Relative Humidity sensor temperature measurement in degrees C O2(%) – Percentage Oxygen measured
xCO2(dry) - Calculated Atmospheric CO2 values
xCO2(wet) - Calculated Water CO2 values
co2kzero - Licor CO2 kzero coefficient co2kspan - Licor CO2 kspan coefficient co2kspan2 - Licor CO2 kspan2 coefficient errors - Error Flags (string)

## “idata” Format

The real-time data, or “Iridium” data is collected during the run when the STATS are computed. After a run is complete, the “idata” command can be sent to retrieve the STATS data. “ts” or “tsq” must be run before this data is valid.. The data has the following format:

"State,Li_Temp_ave(C),Li_Temp_sd,Li_Pres_ave(kPa),Li_Pres_sd,CO2_ave(PPM),CO2_SD,O2_ave(%),O2_S,RH_a ve(%),RH_sd,RH_T_ave(C),Rh_T_sd,Li_RawSample_ave,Li_RawSample_sd,Li_RawDetector_ave,Li_RawReferenc e_sd, SW_xCO2(dry),Atm_xCO2(dry),co2kzero,co2kspan,co2kspan2,eFlags"

Commented [1]: @Matthew.Casari@noaa.gov maybe we need a table at the beginning summarizing all these data output options? Do we have a preferred data option?
_Assigned to Matthew Casari - NOAA Federal_
Commented [2R1]: @noah.lawrence-
slavas@noaa.gov I'm not following what you're asking for. What do you mean by preferred data option? _Reassigned to Noah Lawrence-Slavas - NOAA Federal_
Commented [3R1]: You have added the sdata and idata commands, which behave very differently from the rest of the data formats you are talking about here. This section needs some clarification for how / when the user sees these formats, i.e. report, idata and sdata need to have commands sent to retrieve them. I believe all the other data formats are just printed to the screen after the ts command is given at various times during a measurement cycle. I think a brief headed paragraph explaining this would be very helpful for this section.

31

Where:
State – pCO2 sample mode
Li_Temp_ave(C) – LICOR CO2 sensor chamber temperature in degrees C (mean) Li_Temp_sd - Standard deviation of Licor Temperature
Li_Pres_ave(kPa) - Licor Pressure measured (mean) (kPa)
Li_Pres_sd - Standard Deviation of Licor Pressure measured
CO2_ave(PPM) - CO2 concentration measured (PPM) (mean) CO2_sd- Standard Deviation of CO2 concentration measured O2_ave(%) - Percentage Oxygen measured (mean) O2_sd(%) - Standard deviation of % Oxygen measured.
RH_ave(%) - Percent Relative Humidity measured (mean)
RH_sd - Standard Deviation of Relative Humidity
RH_T_ave(C) - Relative Humidity Sensor Temperature (degC) (mean) RH_T_sd - Standard Deviation of Relative Humidity Temperature Li_RawSample_ave - Licor Raw Sample values(mean) Li_RawSample_sd - Standard deviation of Licor Raw Sample values Li_RawReference_ave -Licor Raw Reference values (mean) Li_RawReference_sd - Standard Deviation of Licor Raw Reference SW_xCO2(dry) – pCO2 value for Seawater
Atm_xCO2(dry) – pCO2 value for Atmosphere
co2kzero - Licor CO2 kzero coefficient
co2kspan - Licor CO2 kspan coefficient co2kspan2 - Licor CO2 kspan2 coefficient

## NetCDF Template Notes

For the Netcdf template we have added a state called 'summary' to the other states (i.e. SPON,SPOFF....). The 'summary' state includes the Dry xCO2 values, the Licor calibration coefficients, the error flags, and the O2cal information for each run. Additionally the NETCDF template includes a 'none' state that is used as a filler value for when the ASVCO2 system is not running.

## ERROR FLAGS Format

At the end of each run, a string containing eight (8) bit-field error code flags is printed. The format of this string is as follows:
FLAGS: [0x0001] [ 0x0002] [0x0004] [0x0008] [ 0x0010] [0x0020] [0x0040] [ 0x0080] Where [0x0001], etc. correspond to the error sub-types (as documented below in the Error Format subsection). Each bit-field is represented as a hexadecimal value. The flag is the bit-wise OR of the errors within the sub-type. For example, a string:

FLAGS: 0000 0000 0400 0000 0000 0000 0201 0000

Would show errors in the 3rd and 7th flags.

A breakdown of these errors would be:

32

[0x0001][0x0000] - PCO2 General Errors: NONE
[0x0002][0x0000] - PCO2 Zero Errors: NONE
[0x0004][0x0400] - PCO2 Span Errors: PCO2 Span Diff Not Met – Span Cal Skipped [0x0008][0x0000] - PCO2 Span2 Errors: NONE
[0x0010][0x0000] - PCO2 Equilibration & Air Errors: NONE
[0x0020][0x0000] - RTC Errors: NONE
[0x0040][0x0201] - Flow Controller, RH & O2 Errors: RH I2C Failure + FLOW Failed to Init [0x0080][0x0000] - Licor Errors: NONE

The 3rd flag corresponds to the PCO2 Span errors. In this case, 0400 is the “Span Diff Not Met – Span Cal Skipped ” error, which indicates that the pressure in the Licor was not sufficiently high enough to allow Span calibration.

The 7th flag was 0201. The 7th flag, or the 0x0040 sub-types (Flow Control, RH & O2 errors) shows a
compound error of 0x0200 | 0x0001 (OR’ed). When split, 0x0200 is a RH I2C Failure and 0x0001 is FLOW
Failed to Init. This would indicate a RH connection error, typically when the RH sensor is not attached to the pCO2 sensor, and a Flow initialization error typical of when the Flow Control is not electrically attached to the pCO2 board.

33

## ERROR CODE Format

Any errors that occur during a system run will be displayed as follows: ERR: [ERROR_CODE] [ERROR_DESCRIPTION]
The ERROR_CODE is broken down as follows:
[ERROR_CODE] = [ERROR_SUBCLASS][ERROR_VALUE]
Where:
ERROR_SUBCLASS and ERROR_VALUE are two 16-bit value in hexadecimal form, concatenated together.

The following is a list sub-classes of errors (First 4 hexadecimal digits in error code):
[0x0001] – PCO2 General Errors
[0x0002] – PCO2 Zero Errors
[0x0004] – PCO2 Span Errors
[0x0008] – PCO2 Span2 Errors
[0x0010] – PCO2 Equilibration & Air Errors [0x0020] – RTC Errors
[0x0040] – Flow Controller, RH & O2 Errors
[0x0080] – Licor Errors
A list of all errors values (last 4 hexadecimal digits) follow in the next section.

EXAMPLE:
The following message would indicate that the Li-COR NDIR Sensor failed during an attempt to calibrate the sensor with the Span gas:
ERR: 00040040 PCO2 Span Failed

This would be broken down as:
ERROR_SUBCLASS = 0x0001
ERROR_VALUE = 0x0040

So the subclass fall under PCO2 General Errors, and the Error Value indicates PCO2 Span Fail

34

## ERROR Codes

## PCO2 General Errors (0x0001)

(XXXX 0000 0000 0000 0000 0000 0000 0000)

CODE | Error String | Description

00010001 00010001 PCO2 Licor Init Fail

| | Error starting the Li-8x0 Sensor
00010002 | 00010002 PCO2 Flow Init Fail | Error starting the Flow Control Module
00010004 | 00010004 PCO2 RH Init Fail | Error starting the Relative Humidity Sensor
00010008 | 00010008PCO2 DL Init Fail | N/A
00010010 | 00010010 PCO2 Config Fail | PCO2 Sensor Configuration Error
00010020 | 00010020 PCO2 Zero Fail | PCO2 Sensor Failure During Zero state
00010040 | 00010040 PCO2 Span Fail | PCO2 Sensor Failure During SPAN state
00010080 | 00010080 PCO2 Span2 Fail | PCO2 Sensor Failure During SPAN2 state
00010100 | 00010100 PCO2 Equil Fail | PCO2 Sensor Failure during Equilibration state
00010200 00010200 PCO2 Air Fail | | PCO2 Sensor failure during Atmospheric air sampling state
00010400 | 00010400 PCO2 Rest Fail | PCO2 Sensor failure to enter rest state
00010800 | 00010800PCO2 Deploy Fail | PCO2 Sensor failure to enter deploy state.
00011000 00011000 PCO2 Flow REST Fail | | PCO2 Flow Control Module failure to enter rest mode
00012000 00012000 PCO2 Flow DPLY Fail | | PCO2 Flow Control Module failure to enter deploy mode
00014000 | 00014000 PCO2 Invalid Mode | PCO2 Invalid state/mode commanded

## PCO2 Zero Errors (0x0002)

(0000 XXXX 0000 0000 0000 0000 0000 0000)

CODE | Error String | Description
00020001 | 00020001 PCO2 Licor Zero Fail | Error zeroing the Li-8x0 Sensor
00020002 | 00020002PCO2 Zero Flow | PCO2 Failure to set Zero flow with pump on in flow

35

| ZERO_ON Fail | controller
00020004 | 00020004 PCO2 Zero SAMPLE 1 Fail | PCO2 failure to read sample from Licor for Zero setting
00020008 | 00020008 PCO2 Zero Flow ZERO_OFF Fail | PCO2 Failure to set Zero flow with pump off in flow controller
00020010 | 00020010 PCO2 Zero Flow PRECAL Fail | PCO2 Failure to set pre-calibration mode for zero in flow controller
00020020 | 00020020 PCO2 Zero SAMPLE 2 Fail | PCO2 failure to sample pre-calibration
00020040 | 00020040 PCO2 Zero CAL Fail | PCO2 failure to calibrate Licor
00020080 | 00020080 PCO2 Zero Flow POSTCAL Fail | PCO2 failure to set post calibration mode
00020100 | 00020100 PCO2 Zero SAMPLE 3 Fail | PCO2 failure to sample post zero calibration

36

## PCO2 Span Errors (0x0004)

(0000 0000 XXXX 0000 0000 0000 0000 0000)

CODE | Error String | Description
00040001 | 00040001 PCO2 Licor Span
Fail
| | Error Spanning the Li-8x0 Sensor
00040002 | 00040002 PCO2 Span Flow SPAN_ON Fail | PCO2 failure to set span mode with open flow from gas canister
00040004 | 00040004 PCO2 Span SAMPLE 1 Fail | PCO2 failure to sample with flow open during span
00040008 | 00040008 PCO2 Span Flow SPAN_OFF Fail | PCO2 failure to close flow from canister during span
00040010 | 00040010 PCO2 Span Flow PRECAL Fail | PCO2 failure to set pre-calibration mode (vent)
00040020 | 00040020 PCO2 Span SAMPLE 2 Fail | PCO2 failure to sample during pre-calibration during span
00040080 | 00040080 PCO2 Span CAL Fail | PCO2 failure to calibrate Licor SPAN
00040100 | 00040100 PCO2 Span Flow POSTCAL Fail | PCO2 failure to set post-calibration mode for SPAN
00040200 | 00040200 PCO2 Span SAMPLE 3 Fail | PCO2 failure to sample after calibration for span
00040400 | 00040400 PCO2 Span Diff Not Met – Span Cal Skipped | The differential pressure (spandiff) was not exceeded (indicating that the span cylinder is likely empty), and the Span calibration was skipped.

37

## PCO2 Span2 Errors (0x0008)

(0000 0000 0000 XXXX 0000 0000 0000 0000)

CODE | Error String | Description
00080001 | 00080001 PCO2 Licor Secondary Span Fail

N/A (Future Use)

00080002 | 00080002 PCO2 Secondary Span Flow SPAN_ON Fail | N/A (Future Use)
00080004 | 00080004 PCO2 Secondary Span SAMPLE 1 Fail | N/A (Future Use)
00080008 | 00080008 PCO2 Secondary Span Flow SPAN_OFF Fail | N/A (Future Use)
00080010 | 00080010 PCO2 Secondary Span Flow PRECAL Fail | N/A (Future Use)
00080020 | 00080020 PCO2 Secondary Span SAMPLE 2 Fail | N/A (Future Use)
00080040 | 00080040 PCO2 Secondary Span CAL Fail | N/A (Future Use)
00080080 | 00080080 PCO2 Secondary Span Flow POSTCAL Fail | N/A (Future Use)
00080100 | 00080100 PCO2 Secondary Span SAMPLE 3 Fail | N/A (Future Use)

38

## PCO2 Equilibrate & Air Errors (0x0010)

(0000 0000 0000 0000 XXXX 0000 0000 0000)

CODE | Error String | Description
00100002 | 00100002 PCO2 Equil Flow EQUIL_ON Fail | PCO2 failure to set equilibration mode with pump on
00100004 | 00100004 PCO2 Equil SAMPLE 1 Fail | PCO2 failure to sample during equilibration mode
00100008 | 00100008 PCO2 Equil Flow EQUIL_OFF 1 Fail | PCO2 failure to shut pump and valves during equilibration mode
00100010 | 00100010 PCO2 Equil Flow VENT Fail | PCO2 failure to set vent state during equilibration
00100020 | 00100020 PCO2 Equil Flow EQUIL_OFF 2 Fail | PCO2 failure to shut pump during equilibration mode
00100040 | 00100040 PCO2 Equil SAMPLE 2 Fail | PCO2 failure to sample during equilibration while vented
00100200 | 00100200 PCO2 Air Flow EQUIL_ON Fail | PCO2 failure to set atmospheric air pump mode
00100400 | 00100400 PCO2 Air SAMPLE 1 Fail | PCO2 failure to sample during atmospheric pumping
00100800 | 00100800 PCO2 Air Flow AIR_OFF 1 Fail | PCO2 failure to
00101000 | 00101000 PCO2 Air Flow VENT Fail | PCO2 failure to vent during air mode
00102000 | 00102000 PCO2 Air Flow AIR_OFF Fail | PCO2 failure to turn pump off during air mode
00104000 | 00104000 PCO2 Air SAMPLE 2 Fail | PCO2 failure to sample while vented during air mode

## RTC Errors (0x0020)

(0000 0000 0000 0000 0000 XXXX 0000 0000)

CODE | Error String | Description
00200002 | 00200002 RTC Alarm Before Current Time | Alarm is set for before the actual current time

39

00200004 | 00200004 RTC Alarm After Current Alarm | Alarm is set for before the expected alarm
00200008 | 00200008 RTC Alarm Repeat = 0 | N/A
00200010 | 00200010 RTC Invalid Month | Month is outside of 1-12
00200020 | 00200020 RTC SQW Invalid Pin | Invalid pin to set square wave for RTC on
00200040 | 00200040RTC Alarm Invalid Pin | Invalid pin to set alarm pin
00200080 | 00200080 RTC Msg Too Long | Message too long for RTC transmission
00200100 | 00200100 RTC Msg Length > Buffer | Message length is longer than buffered data
00200200 | 00200200 RTC Msg Length Too Short | Message length is shorter than buffered data
00200400 | 00200400 RTC I2C Transmission Error | I2C transmission error between microcontroller and RTC
00200800 | 00200800 RTC I2C Receive Error | I2C receive error between microcontroller and RTC
00201000 | 00201000 RTC I2C Hang | I2C is inoperable

## Flow Controller, RH & O2 Errors (0x0040)

(0000 0000 0000 0000 0000 0000 XXXX 0000)

CODE | Error String | Description
00400001 | 00400001 FLOW Failed to Init | Failed to Initialize the Flow Controller
00400002 | 00400002 FLOW Failed on Startup | Flow controller failed on startup
00400004 | 00400004 FLOW Invalid Flow State | Invalid command state for flow controller
00400008 | 00400008 FLOW Mode Set Failure | Failure to set mode in flow controller
00400010 | 00400010 FLOW Message NACK | NACK received from flow controller

40

00400020 | 00400020 FLOW Message Not Sent | Failed to send message to flow controller
00400040 | 00400040 FLOW Mode Not Received | Timeout after sending message to flow controller
00400100 | 00400100 RH Sensor Error | N/A
00400200 | 00400200 RH I2C Failure | RH Sensor I2C fail to connect
00401000 | 00401000 O2 Sensor Failure | N/A

41

## Licor Errors (0x0080)

CODE | Error String | Description
00800002 | 00800002 Invalid Sensor Type | Invalid Licor type specified
00800004 | 00800004 Invalid XML Parent Tag | Failure generating Licor XML parent tag
00800008 | 00800008 Invalid XML Child Tag | Failure generating Licor XML child tag
00800010 | 00800010 Invalid XML LVL3 Tag | Failure generating Licor XML level 3 tag
00800020 | 00800020 Invalid XML Combo | Failure generating Licor XML combination
00800040 | 00800040 Invalid XML Level 1 | Failure validating Licor XML Level 1 tag
00800080 | 00800080 Invalid XML Level 2 | Failure validating Licor XML Level 2 tag
00800100 | 00800100 Invalid XML Level 3 | Failure validating Licor XML Level 3 tag
00800200 | 00800200 Invalid XML Level 4 | Failure validating Licor XML Level 4 tag
00800400 | N/A | N/A
00800800 | N/A | N/A
00801000 | N/A | N/A

42

# Appendix A

## Acronyms

ADC - Analog-to-digital Converter
ASVCO2 – Autonomous Surface Vehicle Carbon Dioxide [Sensor] CO2 – Carbon Dioxide
GPS – Global Positioning System
H20 – Water
ISO-8601- Date Time standard [https://en.wikipedia.org/wiki/ISO_8601] kPa – kilo-pascals
LPM – Low Power Mode
mA – milli-amp
M2M - Machine to Machine
MBARI – Monterey Bay Aquarium Research Institute NOAA - National Oceanic and Atmospheric Administration O2 - Oxygen
PCB - Printed Circuit Board
pCO2 – Partial pressure of Carbon Dioxide
PMEL - Pacific Marine Environmental Laboratory ppm – Parts per million (equivalent to μmol mol⁻¹) RH – Relative Humidity
RTC - Real-time Clock
Span – Calibration of CO2 sensor with precision WMO certified CO2 concentration sample uA – micro-amp
VDC – Volts Direct Current
XML – Extensible Markup Language
WMO – World Meteorological Organization
Zero – Calibration of CO2 sensor with known concentration of ~0.0μmol mol-1

43

# Appendix B

## Li-Cor Configuration

The following is the list of the Li-Cor configurations set prior to a sample. All have a root of li830.

Parent | Child | Value | XML
rs232 | co2 | true | <li830><rs232><co2>true</co2></rs232></li830>
rs232 | co2abs | true | <li830><rs232><co2abs>true</co2abs></rs232></li830>
rs232 | celltemp | true | <li830><rs232><celltemp>true</celltemp></rs232></li830>
rs232 | cellpres | true | <li830><rs232><cellpres>true</cellpres></rs232></li830>
rs232 | ivolt | true | <li830><rs232><ivolt>true</ivolt></rs232></li830>
rs232 | echo | false | <li830><rs232><echo>echo</echo></rs232></li830>
rs232 | strip | false | <li830><rs232><strip>false</strip></rs232></li830>
rs232 | flowrate | false | <li830><rs232><flowrate>false</flowrate></rs232></li830>
rs232 | raw | true | <li830><rs232><raw>true</raw></rs232></li830>
cfg | outrate | 0.0 | <li830><cfg><outrate>0.0</outrate></cfg></li830>
cfg | heater | false | <li830><cfg><heater>false</heater></cfg></li830>
cfg | pcomp | true | <li830><cfg><pcomp>true</pcomp></cfg></li830>
cfg | filter | 0.0 | <li830><cfg><filter>0.0</filter></cfg></li830>
cfg | bench | 14 | <li830><cfg><bench>14</bench></cfg></li830>
cfg | alarms | false | <li830><cfg><alarms>false</alarms></cfg></li830>
cfg | span | 0.0 | <li830><cfg><span>0.0</span></cfg></li830>

44

# Appendix C

## Flow Diagrams

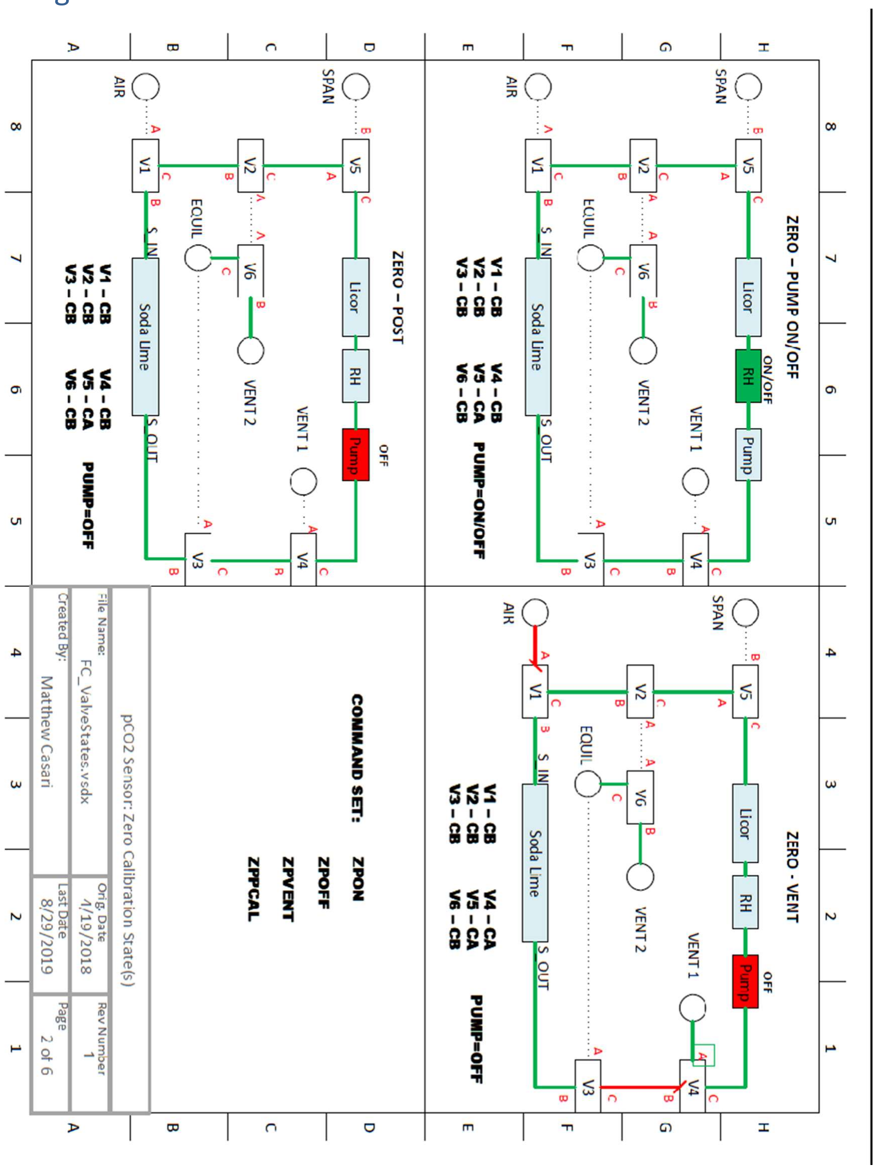
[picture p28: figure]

45

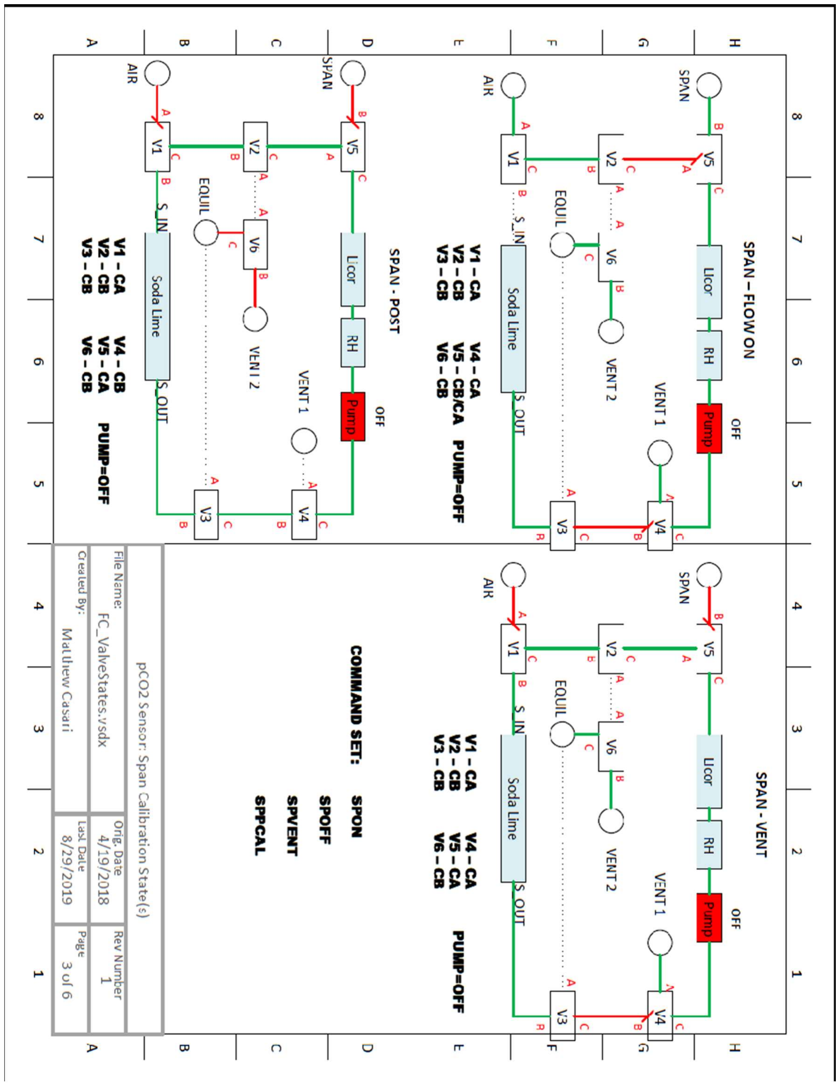
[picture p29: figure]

46

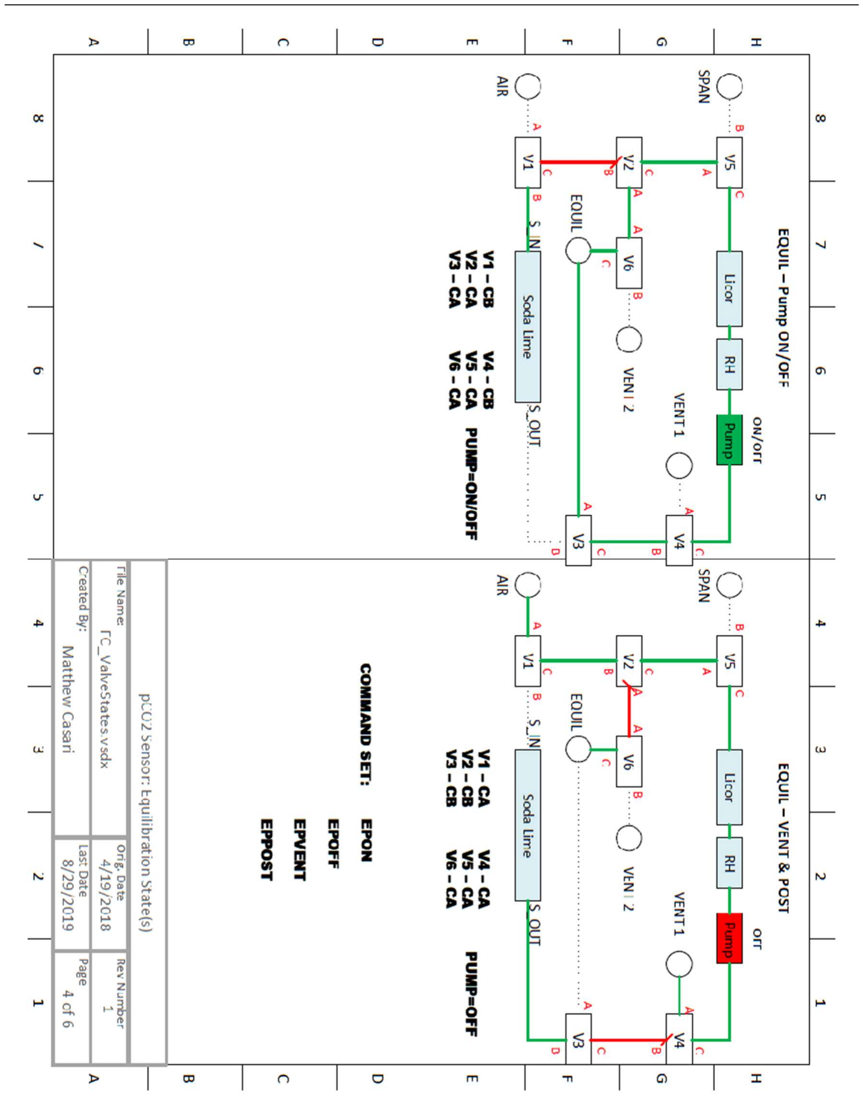
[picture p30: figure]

47

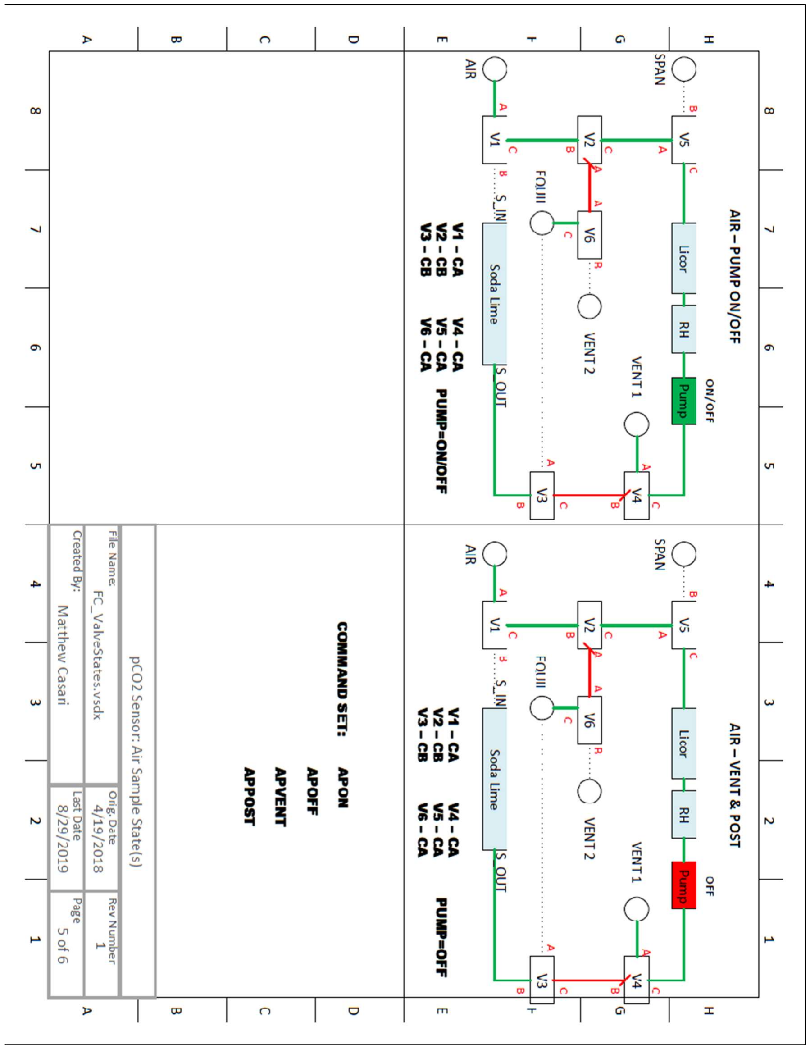
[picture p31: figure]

48

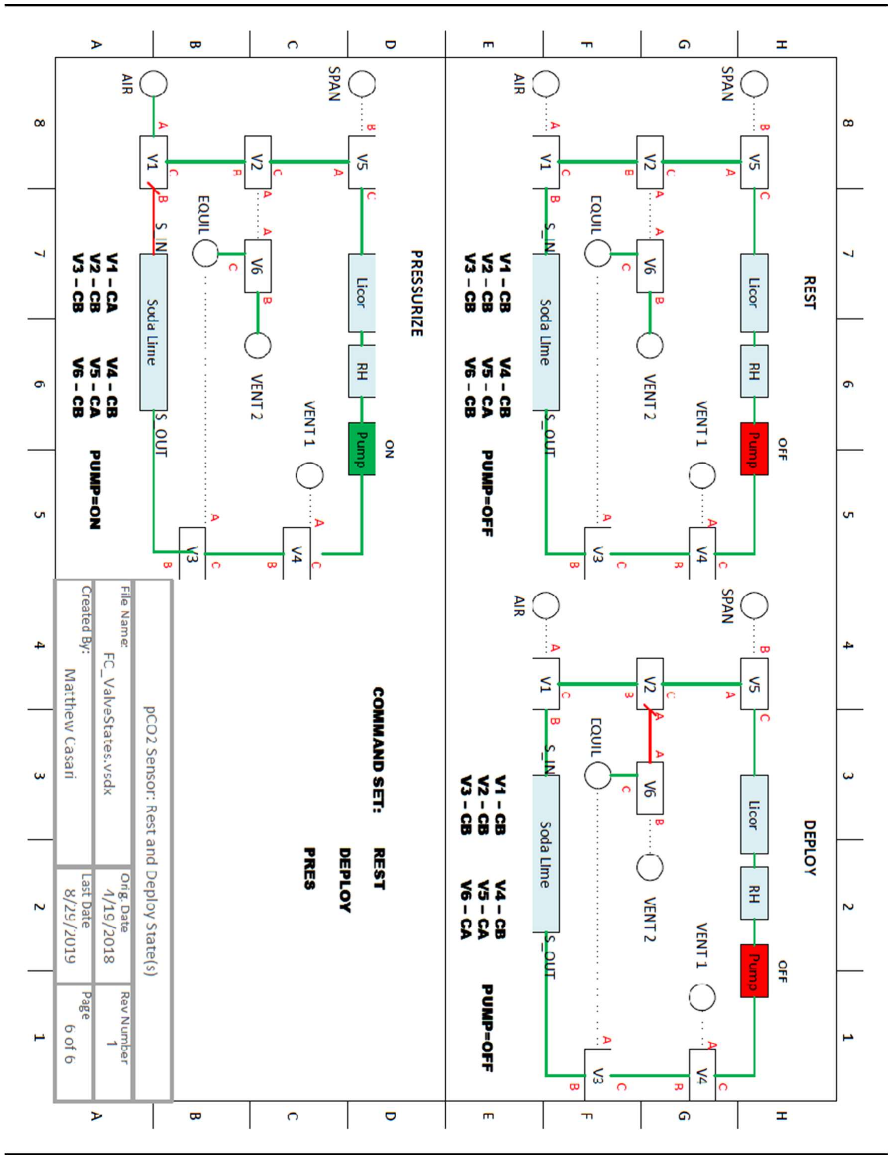
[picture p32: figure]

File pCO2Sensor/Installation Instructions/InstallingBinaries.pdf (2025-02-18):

# MSP430 Programming Instructions

PMEL's Engineering Development Division uses MSP430 microcontrollers in many of the custom circuits. The following is the procedure for programming the microcontrollers, also known as "flashing".

## Requirements

The following are the basic hardware and software requirements for loading binary files onto the microcontroller.

Hardware

Texas Instruments MSP-FET Flash Emulation Tool
EDD Custom 0.100" Pitch x14-pin to 0.050" pitch x10-pin converter

Software

Elprotronic, Inc. FET-Pro-430-LITE
Free download from www.elprotronic.com

Files

Pre-generated binary files for target device
File should have the form "DeviceName_version.txt

## Loading "Binary" files to target

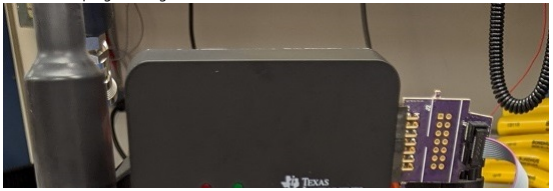
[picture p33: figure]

1. Connect the programming cable to the microcontroller and the MSP-FET.

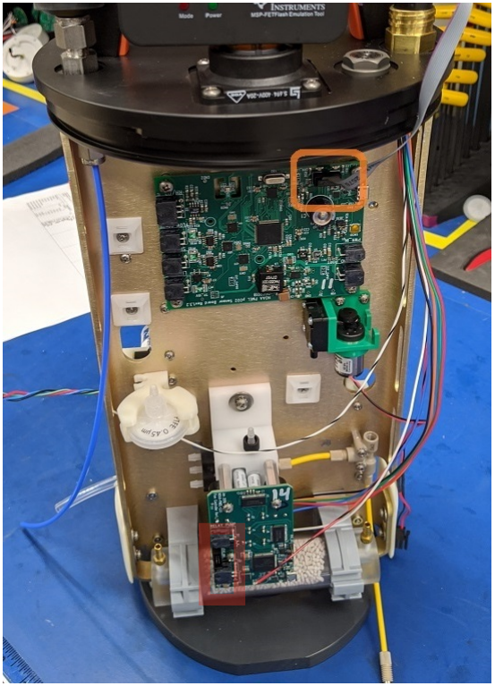
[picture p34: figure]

2. Apply Power to the target board
3. Open the FET-Pro-430 program
4. Press the button "Open Code File ->", navigate to the location of the "binary" file (ProjectName.txt)


5. In the Microcontroller Type block (refer to User Manual for values)

* In "Group", select the general type of MSP430 used.
* On the next line, select the specific type of MSP430 used


1. In the "Device Action" block, press "AUTO PROG."

* If successfull, the "Status" block should show **"Pass"** * If unsuccessfull, press "ERASE FLASH" and try step 6 again.


1. The device is now programmed

NOTE: The board may require additional configuration settings over the console. Consult the User Manual for the corresponding device.

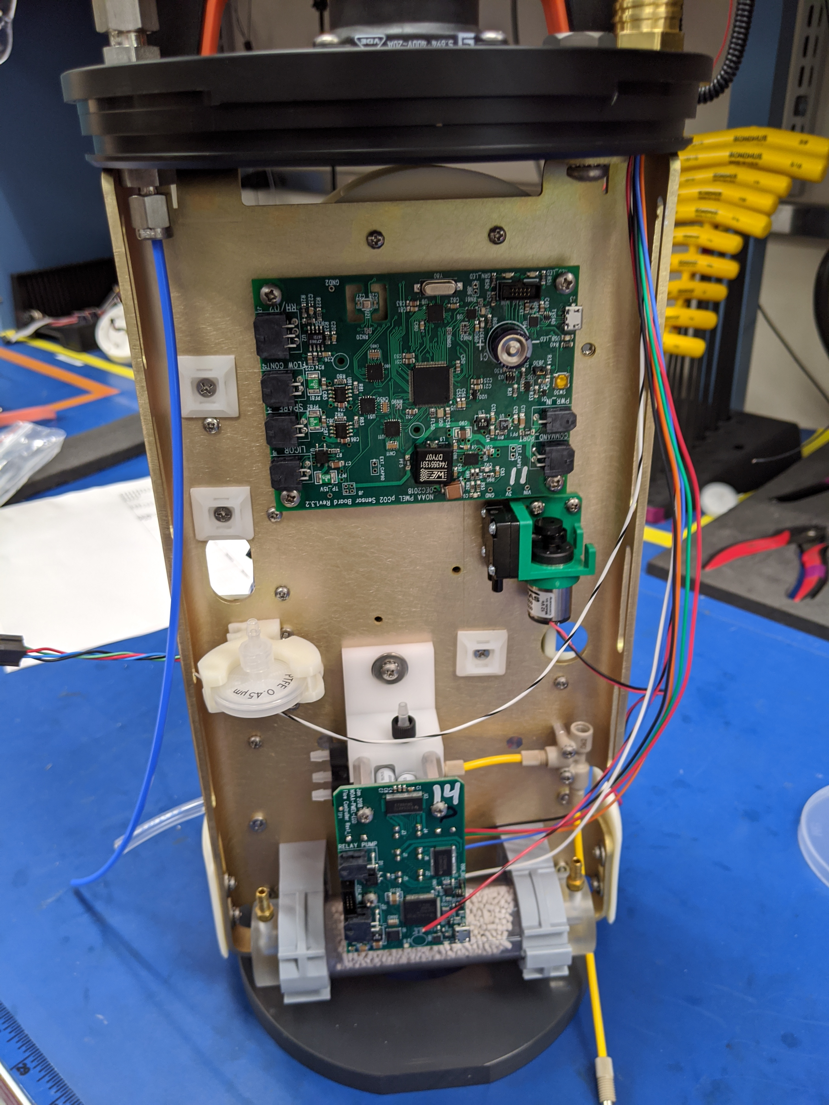
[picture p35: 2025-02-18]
pCO2Sensor/Installation Instructions/Images/PCO2_No_Programmer.jpg

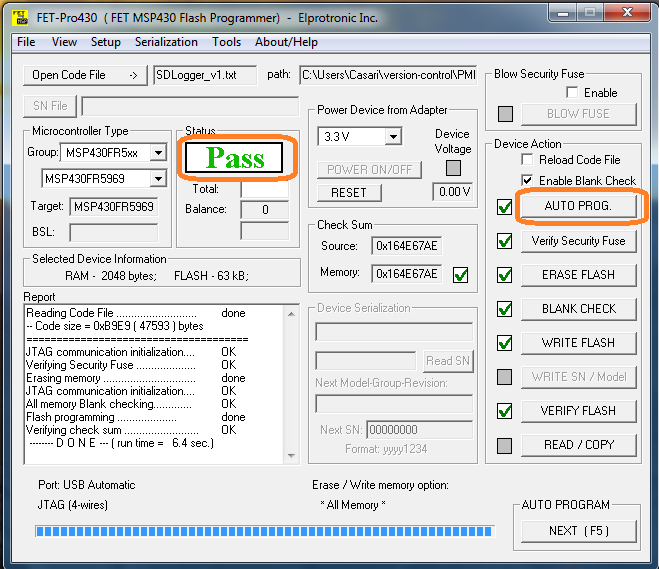
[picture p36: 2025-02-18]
FlowController/Firmware/Binaries/Images/FET_Pro430_Step4.png

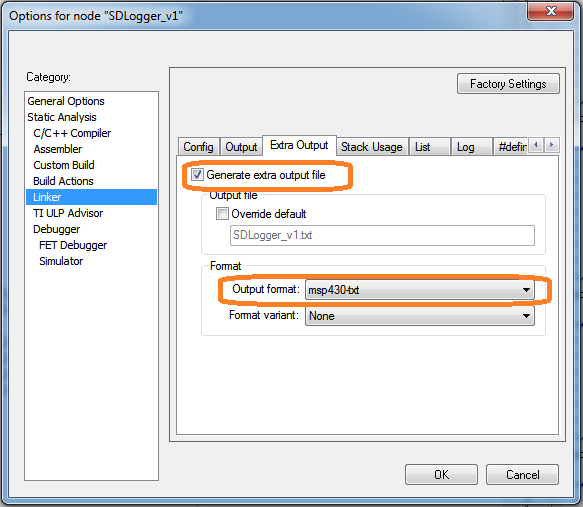
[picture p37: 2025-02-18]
pCO2Sensor/Installation Instructions/Images/Linker_2.png

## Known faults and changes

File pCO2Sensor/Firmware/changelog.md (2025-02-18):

# Change Log for pCO2 Firmware
## v1.11-29
Adding Licor CO2 Polynomial values ccva1/2/3/4 to the report.
## v1.11-27
Fixing garbage characters in output.  
## v1.11-21
Fixing mfr command missing from report & commands
## v1.11-16
Fixing issue with idata/sdata not reporting in v1.11
## v1.11-10
Escape character (0x1b) sent 3 times will now reset the system.

## v1.11-8
Bug fixes.

### Added
* Added Ctrl-Z x3 as alternate restart command for command(rs-232) only.
### Fixed
* tsq created unrecoverable message verbosity.  Fixed.
* fcurrent/fpulse not showing on first call.  Added flow control restart for that.  Needs to be in test mode.

## v1.11
v1.11 added capability to the Flow Controller interface as well as addressed logging on the command port and a few error messages.
### Added
* [Issue #220](https://github.com/NOAA-PMEL/EDD-pCO2Sensor/issues/220).  Updated pCO2 firmware with Drying/Purge functionality recently added to Flow Control firmware.  New functions for running with purge are "Take Sample with Purge" (```>tsp```)  and "Take Sample Quiet with Purge" (```>tspq```) 
* [Issue #227](https://github.com/NOAA-PMEL/EDD-pCO2Sensor/issues/227). Logging interface for RS232.  Can now set the command port log level (debug or error) using ```>log= debug``` or ```>log= error``` in console.  Debug mode provides highest verbosity logging.  Error provides only data and error messages.
  
* Flow Controller pass-through mode now allows direct communication with flow control board. ```> flowpass``` puts the pCO2 board into this mode.
*  Flow pulse and Flow current now allows direct setting of these Flow Control board parameters.  ```fpulse= XXX``` sets the valve pulse length to XXX.  ```fcurrent= X``` sets the clipping current to X (0 - 7).
*  
### Changed
*  Logging module refactored.  Removed unnecessary codes and errors.c/h files which were confusing duplicates of logging.c/h.   

### Fixed
* Errors
---
## v1.10 
v1.10 primarily added functionality for integrating with the TELOS buoy controller.
### Added
* SPON time now settable. (Allows for user define Span Gas ON time to be modified for different field conditions).
### Changed
* IData and SData commands updated to interface with TELOS buoy controller
* Sample rate updated
 
### Fixed
* TS hang issue.

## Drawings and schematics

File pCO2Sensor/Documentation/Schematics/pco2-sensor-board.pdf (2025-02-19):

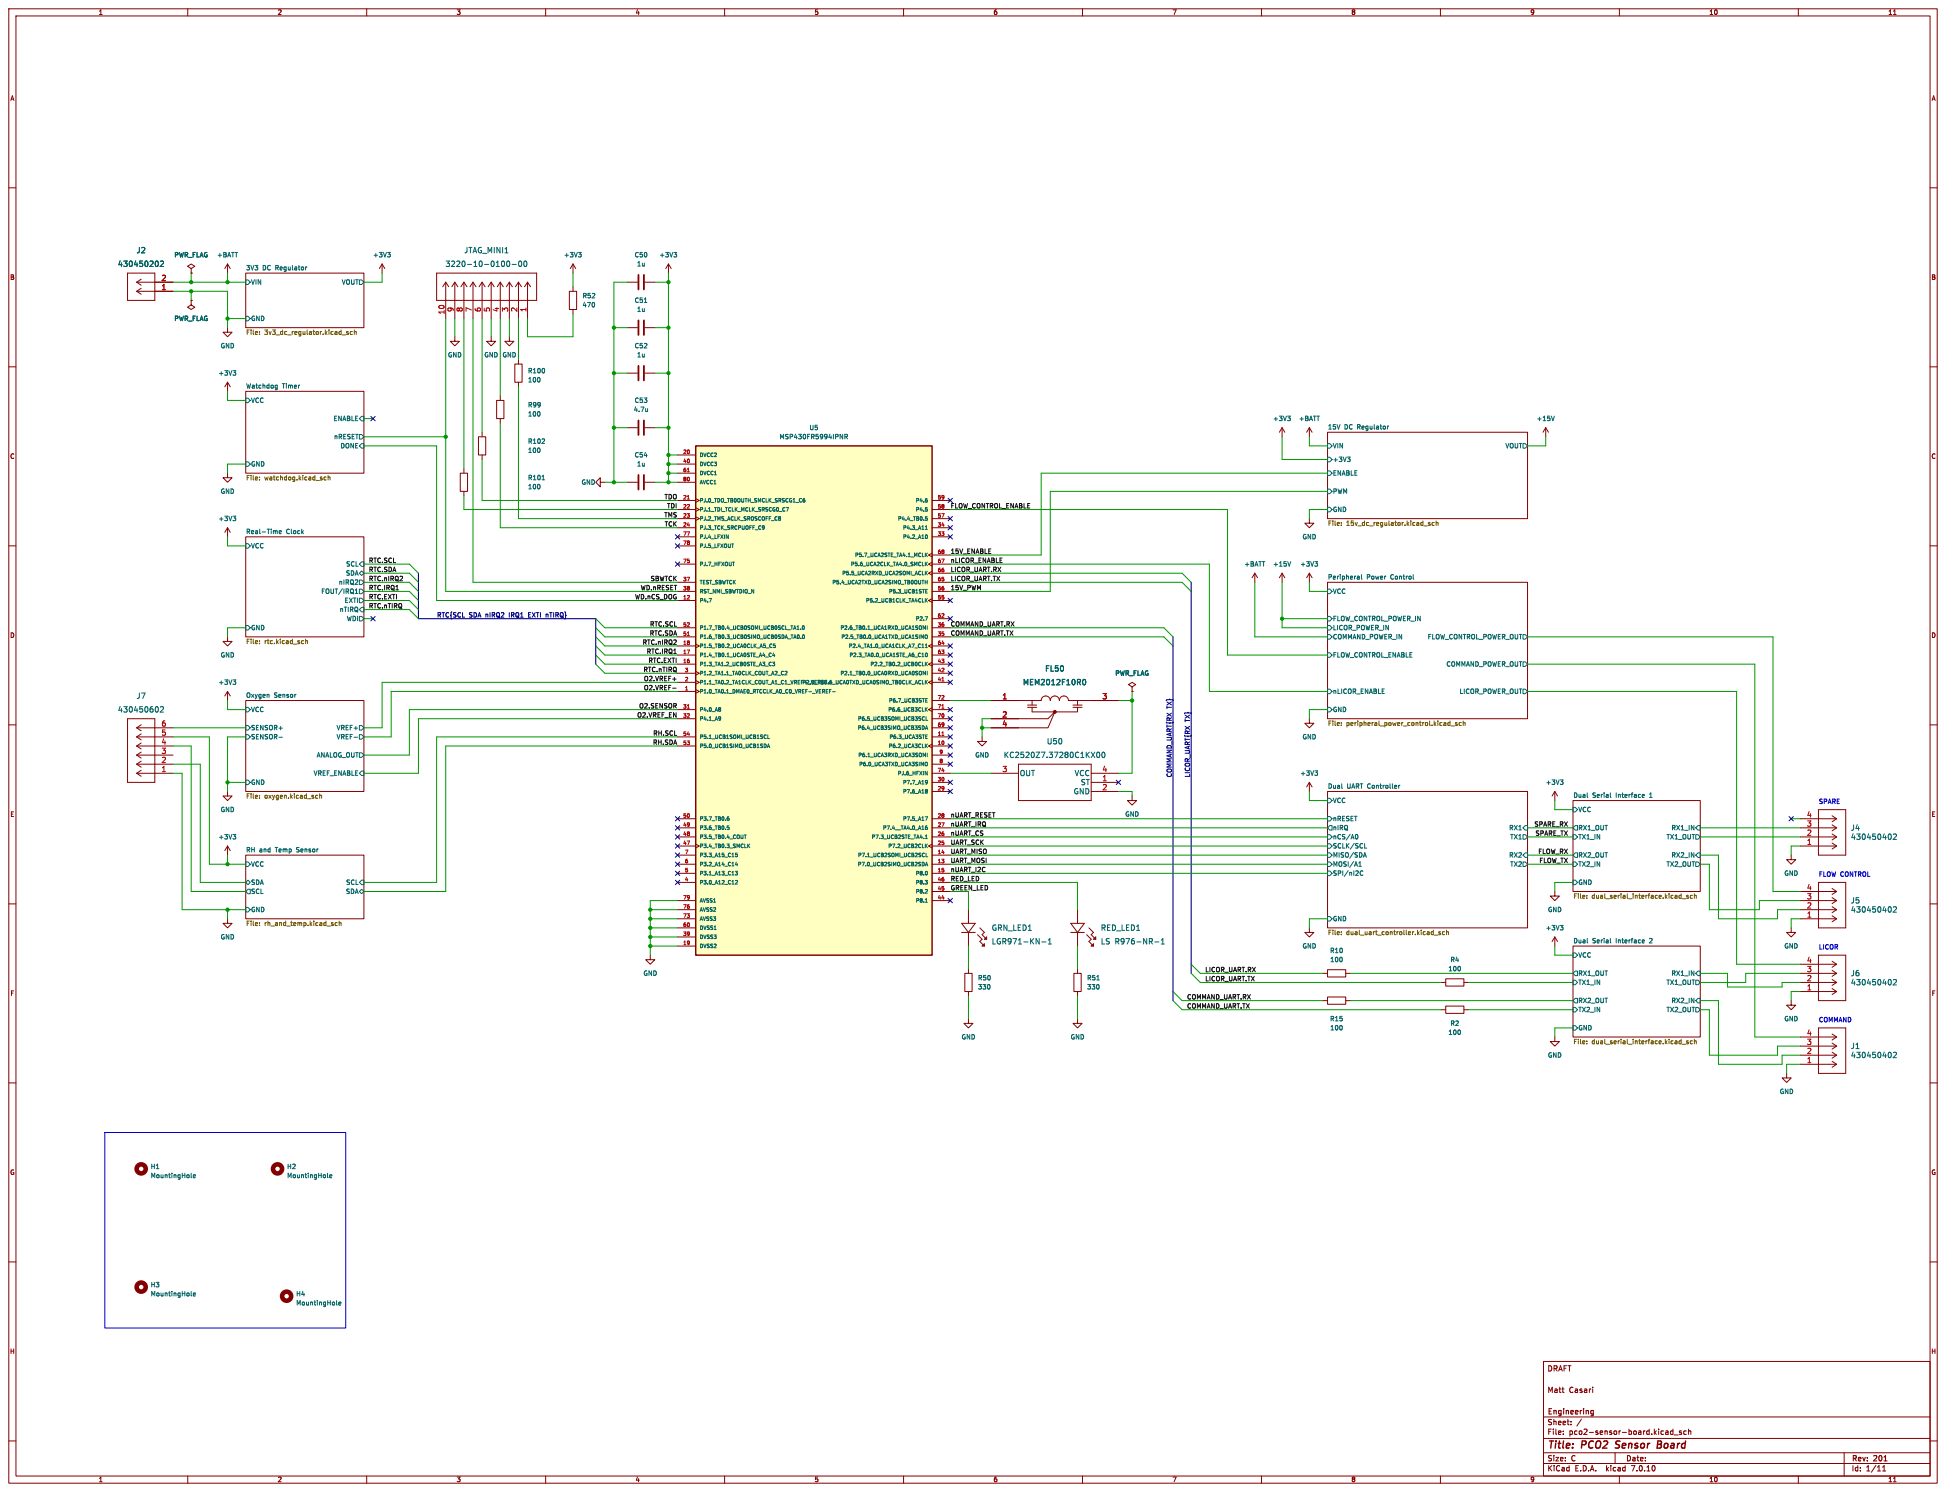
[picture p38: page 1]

3V3 DC Regulator File: 3v3_dc_regulator.kicad_sch VCC GND

TDI RTC.IRQ1 RTC.EXTI RTC.nIRQ2

TMS
TCK
RH.SDA RTC.EXTI RTC.IRQ1 O2.VREF+ WD.nRESET WD.nCS_DOG

TX2 TX1 RX2 RX1 Dual UART Controller File: dual_uart_controller.kicad_sch VCC

RH and Temp Sensor File: rh_and_temp.kicad_sch

File: pco2-sensor-board.kicad_sch Sheet: / Engineering Matt Casari DRAFT

Id: 1/11 Title: PCO2 Sensor Board

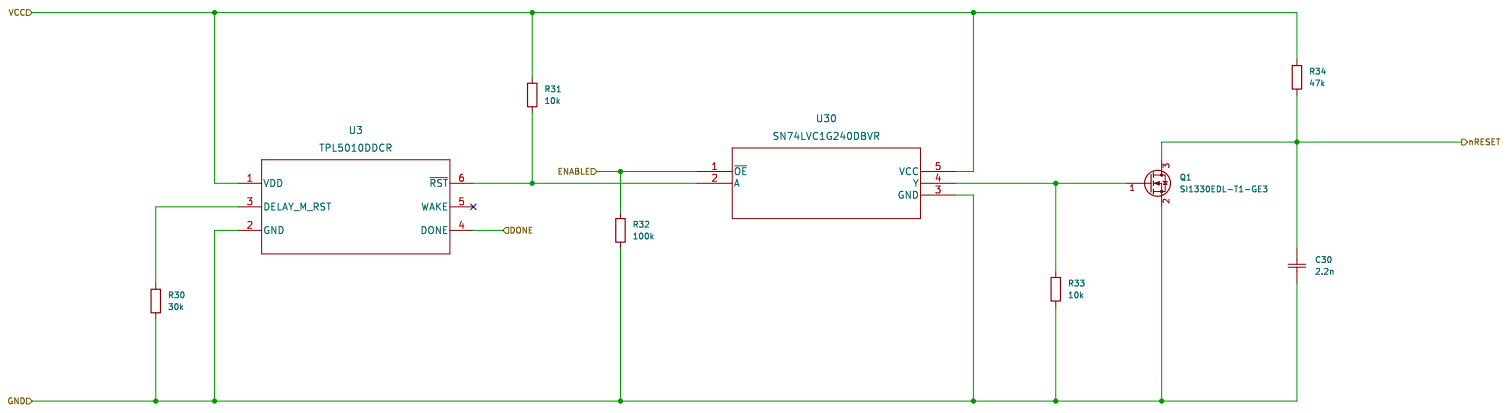
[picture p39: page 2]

Id: 2/11 Title: PCO2 Sensor Board

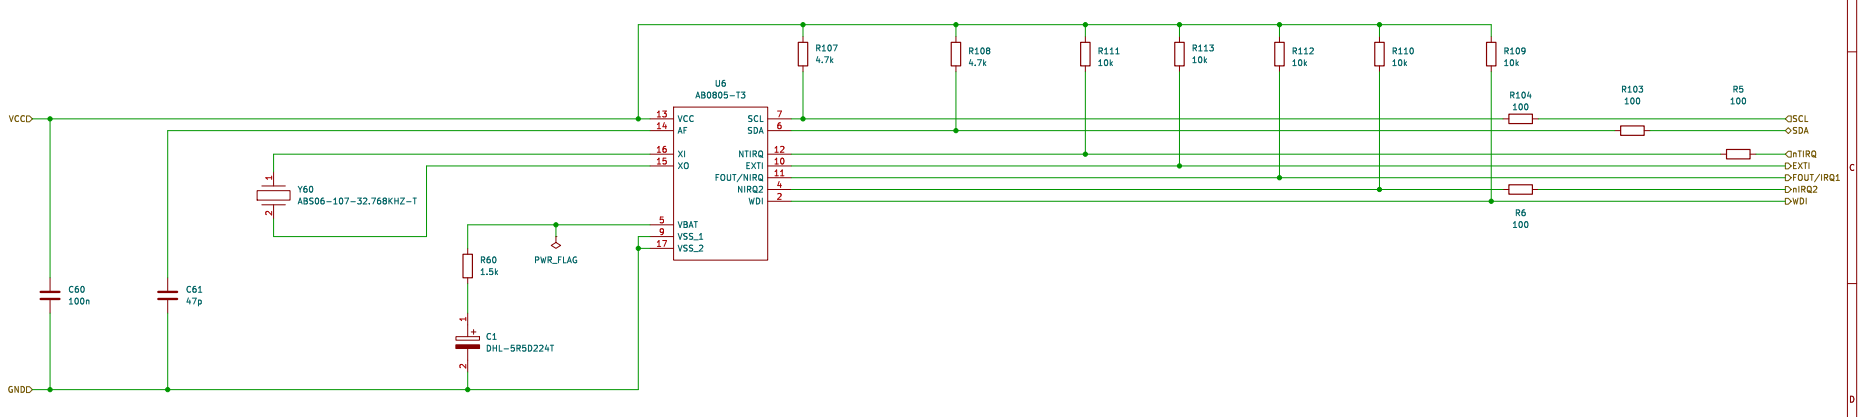
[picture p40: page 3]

1 2 Y60 ABS06-107-32.768KHZ-T EXTI 10 FOUT/NIRQ 11 NTIRQ 12 VCC 13 AF 14 XO 15 XI 16 VSS_2 17 WDI 2 NIRQ2 4 VBAT 5 SDA 6 SCL 7 VSS_1 9 U6 AB0805-T3 R108

FOUT/IRQ1 SCL WDI EXTI nTIRQ
SDA

Id: 3/11 Title: PCO2 Sensor Board

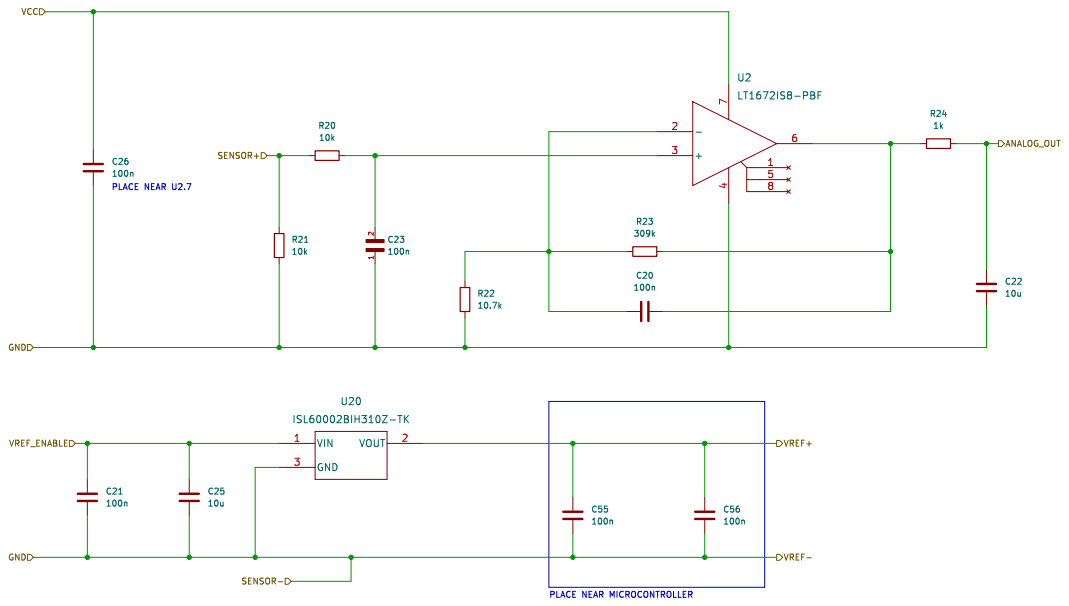
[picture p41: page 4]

Id: 4/11 Title: PCO2 Sensor Board

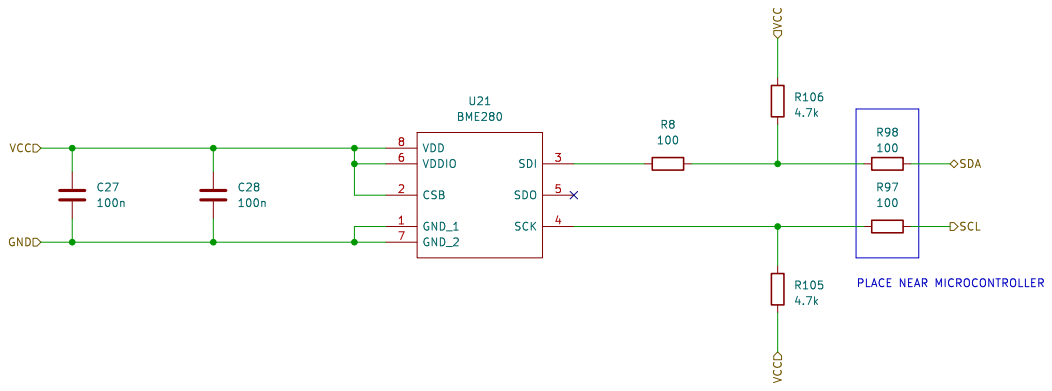
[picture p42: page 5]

Id: 5/11 Title: PCO2 Sensor Board

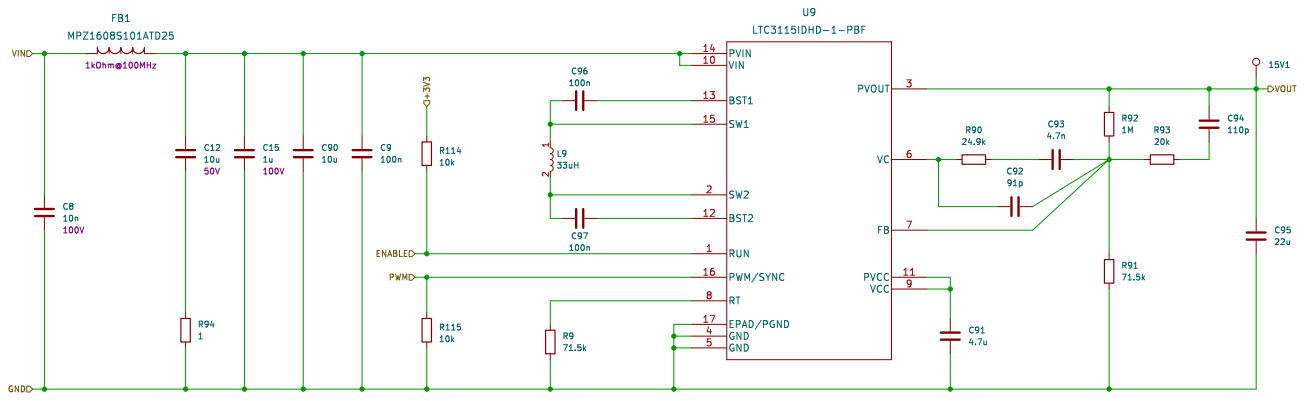
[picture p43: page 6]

Engineering Matt Casari DRAFT R115

Id: 6/11 Title: PCO2 Sensor Board

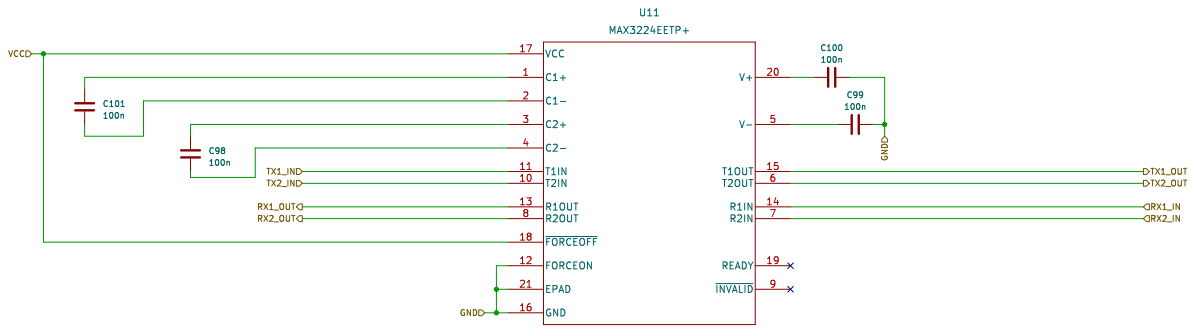
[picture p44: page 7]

Id: 7/11 Title: PCO2 Sensor Board

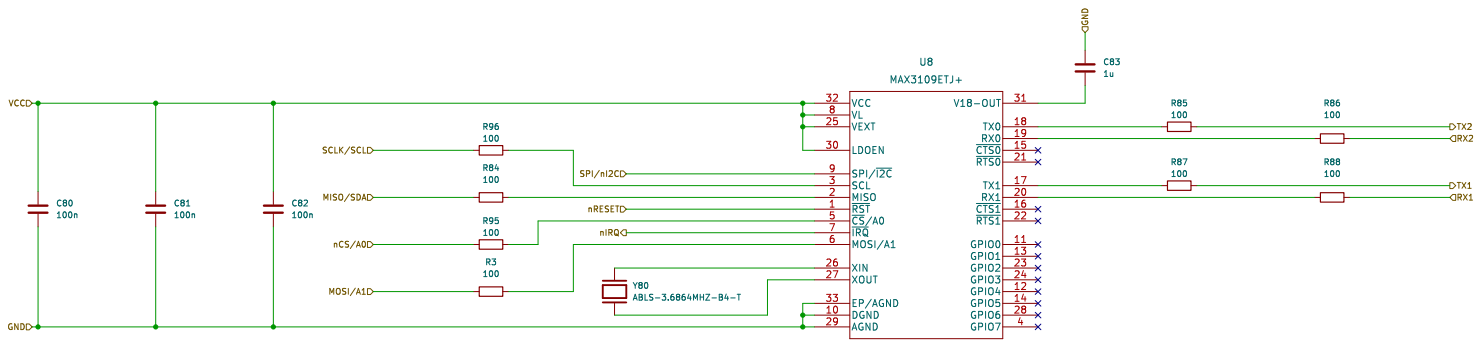
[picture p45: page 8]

Id: 8/11 Title: PCO2 Sensor Board

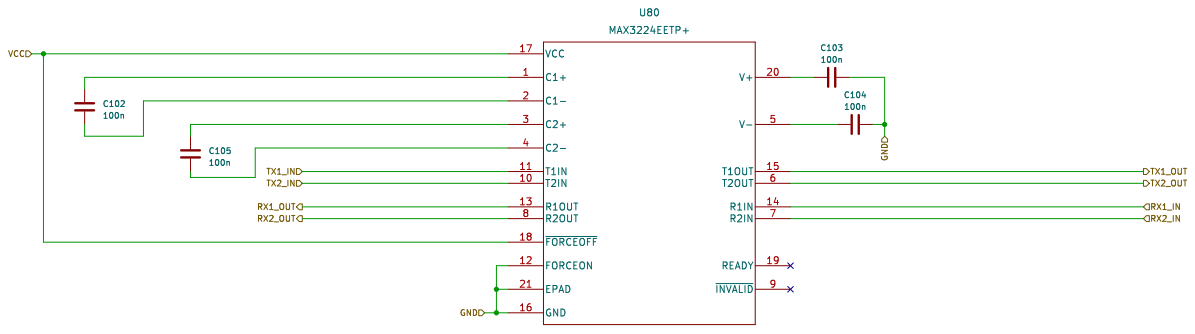
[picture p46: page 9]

Id: 9/11 Title: PCO2 Sensor Board

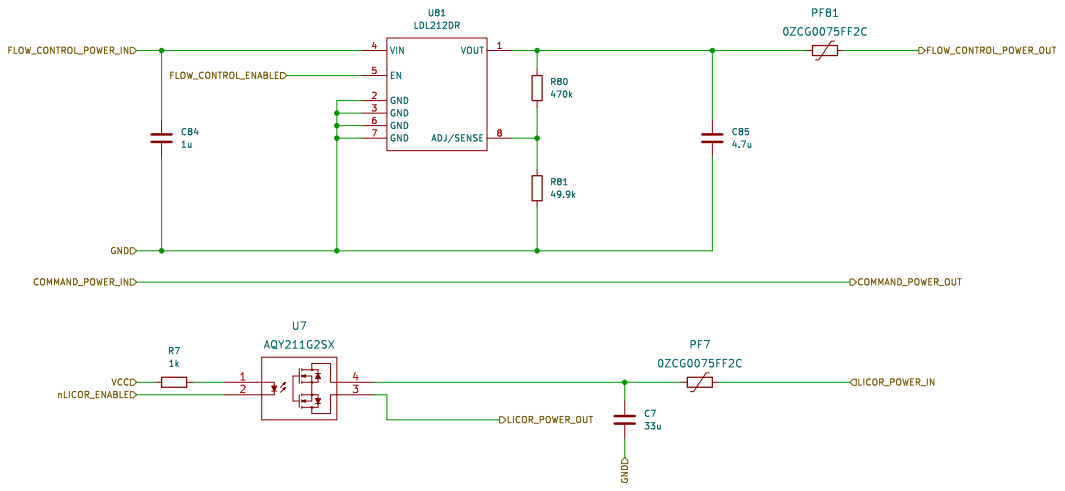
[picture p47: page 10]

Id: 10/11 Title: PCO2 Sensor Board

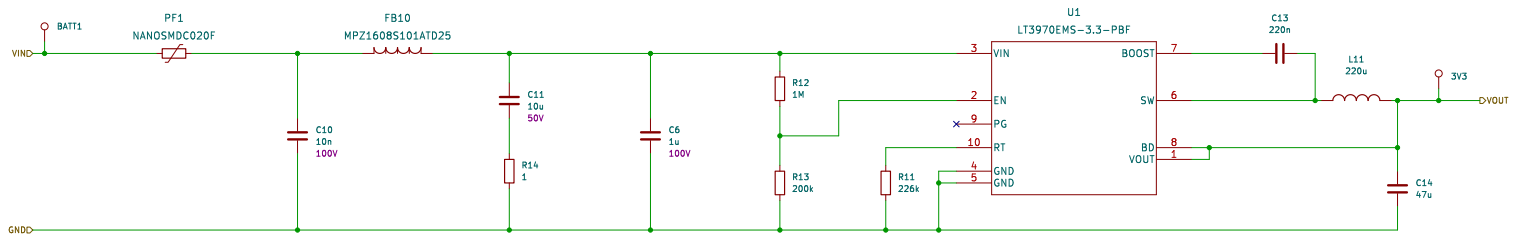
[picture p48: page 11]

Engineering Matt Casari DRAFT

Id: 11/11 Title: PCO2 Sensor Board

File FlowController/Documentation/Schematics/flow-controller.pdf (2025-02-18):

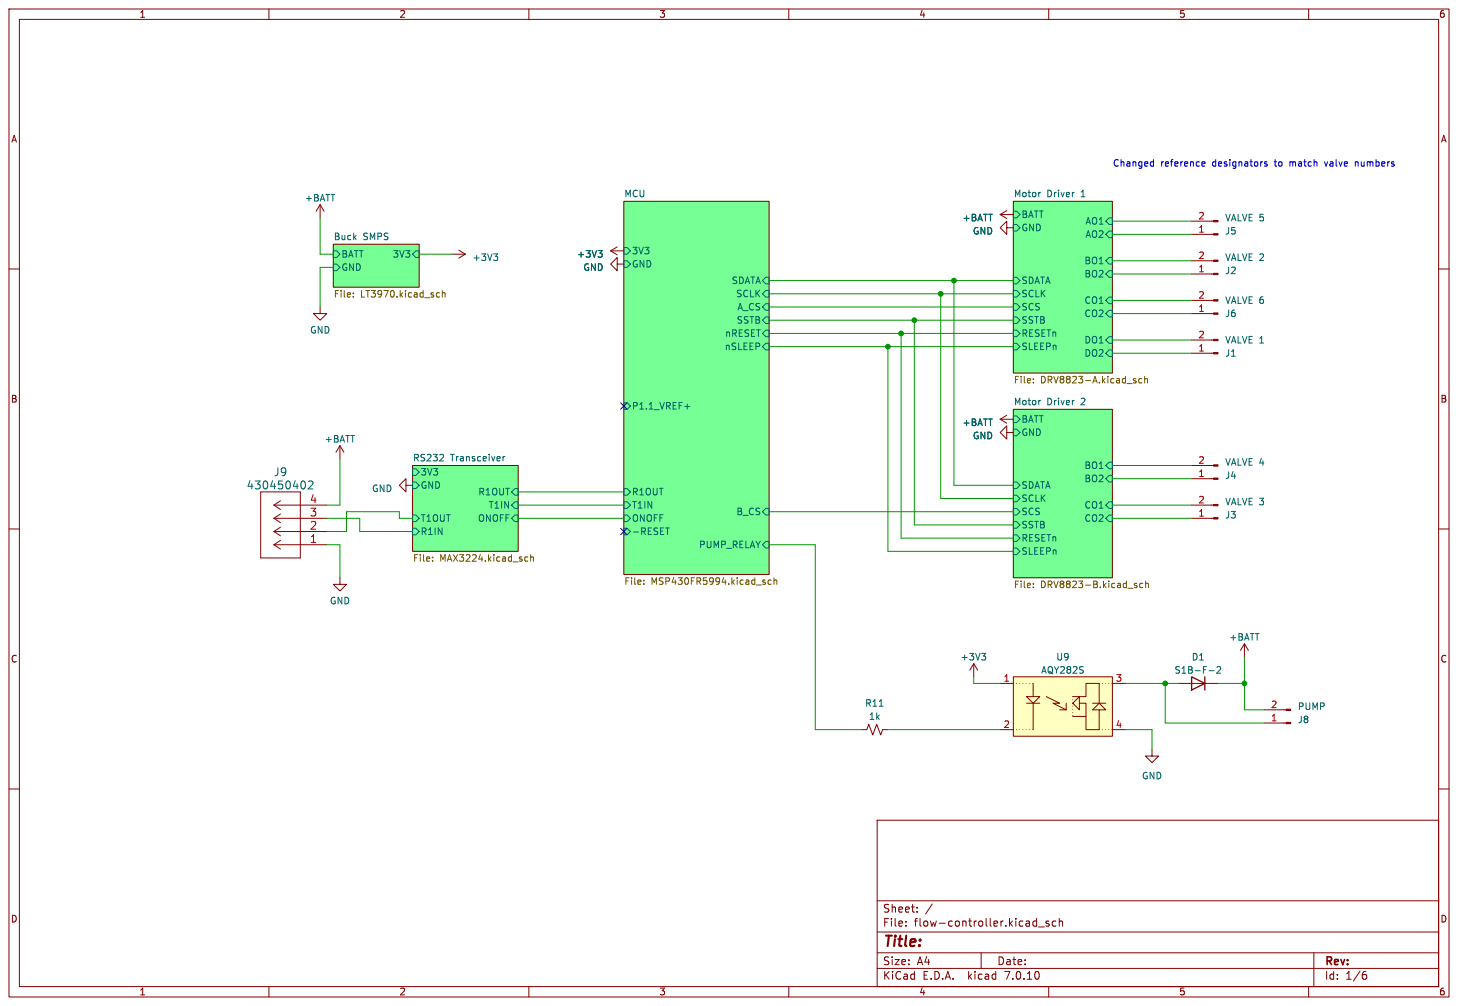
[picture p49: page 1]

Id: 1/6 Title: File: flow-controller.kicad_sch Sheet: / ONOFF


Id: 2/6 Title: File: MSP430FR5994.kicad_sch Sheet: /MCU/





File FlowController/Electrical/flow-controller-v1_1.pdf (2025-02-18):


J3VALVE 3 +3V3
CO2 BO2 BO1 CO1 Motor Driver 2 File: DRV8823-B.kicad_sch GND

Id: 1/6 Title: File: flow-controller.kicad_sch Sheet: / ONOFF






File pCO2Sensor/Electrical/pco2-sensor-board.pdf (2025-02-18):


RTC.SCL TMS WD.nRESET

RTC.EXTI RTC.nTIRQ

TX2 TX1 RX2 RX1 Dual UART Controller File: dual_uart_controller.kicad_sch VCC GND

RH and Temp Sensor File: rh_and_temp.kicad_sch

File: pco2-sensor-board.kicad_sch Sheet: / Engineering Matt Casari DRAFT

Id: 1/11 Title: PCO2 Sensor Board


Id: 2/11 Title: PCO2 Sensor Board


1 2 Y60 ABS06-107-32.768KHZ-T EXTI 10 FOUT/NIRQ 11 NTIRQ 12 VCC 13 AF 14 XO 15 XI 16 VSS_2 17 WDI 2 NIRQ2 4 VBAT 5 SDA 6 SCL 7 VSS_1 9 U6 AB0805-T3 R111

FOUT/IRQ1 SCL WDI EXTI nTIRQ
SDA

Id: 3/11 Title: PCO2 Sensor Board


Id: 4/11 Title: PCO2 Sensor Board


Id: 5/11 Title: PCO2 Sensor Board


Engineering Matt Casari DRAFT R115

Id: 6/11 Title: PCO2 Sensor Board


Id: 7/11 Title: PCO2 Sensor Board


Id: 8/11 Title: PCO2 Sensor Board


Id: 9/11 Title: PCO2 Sensor Board


Id: 10/11 Title: PCO2 Sensor Board


Engineering Matt Casari DRAFT

Id: 11/11 Title: PCO2 Sensor Board

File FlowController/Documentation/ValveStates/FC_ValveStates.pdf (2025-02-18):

# National Oceanic and Atmospheric Administration

# Pacific Marine Environmental Lab

7600 Sand Point Way NE
Bldg 3/EDD
Seattle, WA 98115

Address:

(206)526-6700
Fax – (206)526-6744

Phone:

Project:

FC_ValveStates.vsdx | 8/29/2019
File Name: | Orig. Date | Rev Number
Matthew Casari | 8/29/2019 | 1 of 6
Created By: | Last Date | Page

# National Oceanic and Atmospheric Administration

# Pacific Marine Environmental Lab

7600 Sand Point Way NE
Bldg 3/EDD
Seattle, WA 98115

Address:

(206)526-6700
Fax – (206)526-6744

Phone:

Project:

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

## pCO2 Valve States

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
8 | 7 | 6 | 5 | 4 | 3 | 2 | 1

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
# PCO2 Flow Controller Valve States

### SPAN

V5

AIR; Licor; Pump; Soda Lime; EQUIL; VENT 2; VENT 1; SPAN; ZERO – PUMP ON/OFF; ZERO - VENT; ZERO – POST; ON/OFF; OFF; PUMP=OFF; FC_ValveStates.vsdx; File Name:; Orig. Date; Rev Number; Matthew Casari; Created By:; Last Date; Page; S_OUT; COMMAND SET:; ZPON; ZPOFF; ZPVENT; ZPPCAL

PUMP=ON/OFF

pCO2 Sensor: Zero Calibration State(s)

V4

### VENT 1

SPAN; AIR; Licor; Pump; Soda Lime; EQUIL; VENT 2; VENT 1; SPAN - VENT; SPAN - POST; OFF; PUMP=OFF; FC_ValveStates.vsdx; File Name:; Orig. Date; Rev Number; Created By:; Last Date; Page; S_OUT; COMMAND SET:; SPON; SPOFF; SPVENT; SPPCAL

SPAN – FLOW ON

pCO2 Sensor: Span Calibration State(s)

V4

### VENT 1

SPAN; AIR; Licor; Pump; Soda Lime; EQUIL; VENT 2; VENT 1; EQUIL – Pump ON/OFF; EQUIL – VENT & POST; ON/OFF; OFF; PUMP=OFF; FC_ValveStates.vsdx; File Name:; Orig. Date; Rev Number; Created By:; Last Date; Page; S_OUT; COMMAND SET:; EPON; EPOFF; EPVENT; EPPOST

PUMP=ON/OFF

pCO2 Sensor: Equilibration State(s)

V4

### VENT 1

SPAN; AIR; Licor; Pump; Soda Lime; EQUIL; VENT 2; VENT 1; AIR – PUMP ON/OFF; AIR – VENT & POST; ON/OFF; OFF; PUMP=OFF; FC_ValveStates.vsdx; File Name:; Orig. Date; Rev Number; Created By:; Last Date; Page; S_OUT; COMMAND SET:; APON; APOFF; APVENT; APPOST

PUMP=ON/OFF

pCO2 Sensor: Air Sample State(s)

V4

### VENT 1

SPAN; AIR; Licor; Pump; Soda Lime; EQUIL; VENT 2; VENT 1; REST; DEPLOY; OFF; PUMP=OFF; FC_ValveStates.vsdx; File Name:; Orig. Date; Rev Number; Created By:; Last Date; Page; PRESSURIZE; PUMP=ON; S_OUT; COMMAND SET:; PRES

pCO2 Sensor: Rest and Deploy State(s)

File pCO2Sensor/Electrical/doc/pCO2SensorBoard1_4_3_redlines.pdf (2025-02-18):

## Watch Dog Timer

# P5.0/UCB1SIMO/UCB1SDA DVCC¹


7600 Sand Point Way NE
Seattle, WA 98115

## FlowCont-RS232

## I2C to Quad UART Interface


RH and Temp Sensor

C28 VDDio GND GND VDD

7600 Sand Point Way NE
Seattle, WA 98115

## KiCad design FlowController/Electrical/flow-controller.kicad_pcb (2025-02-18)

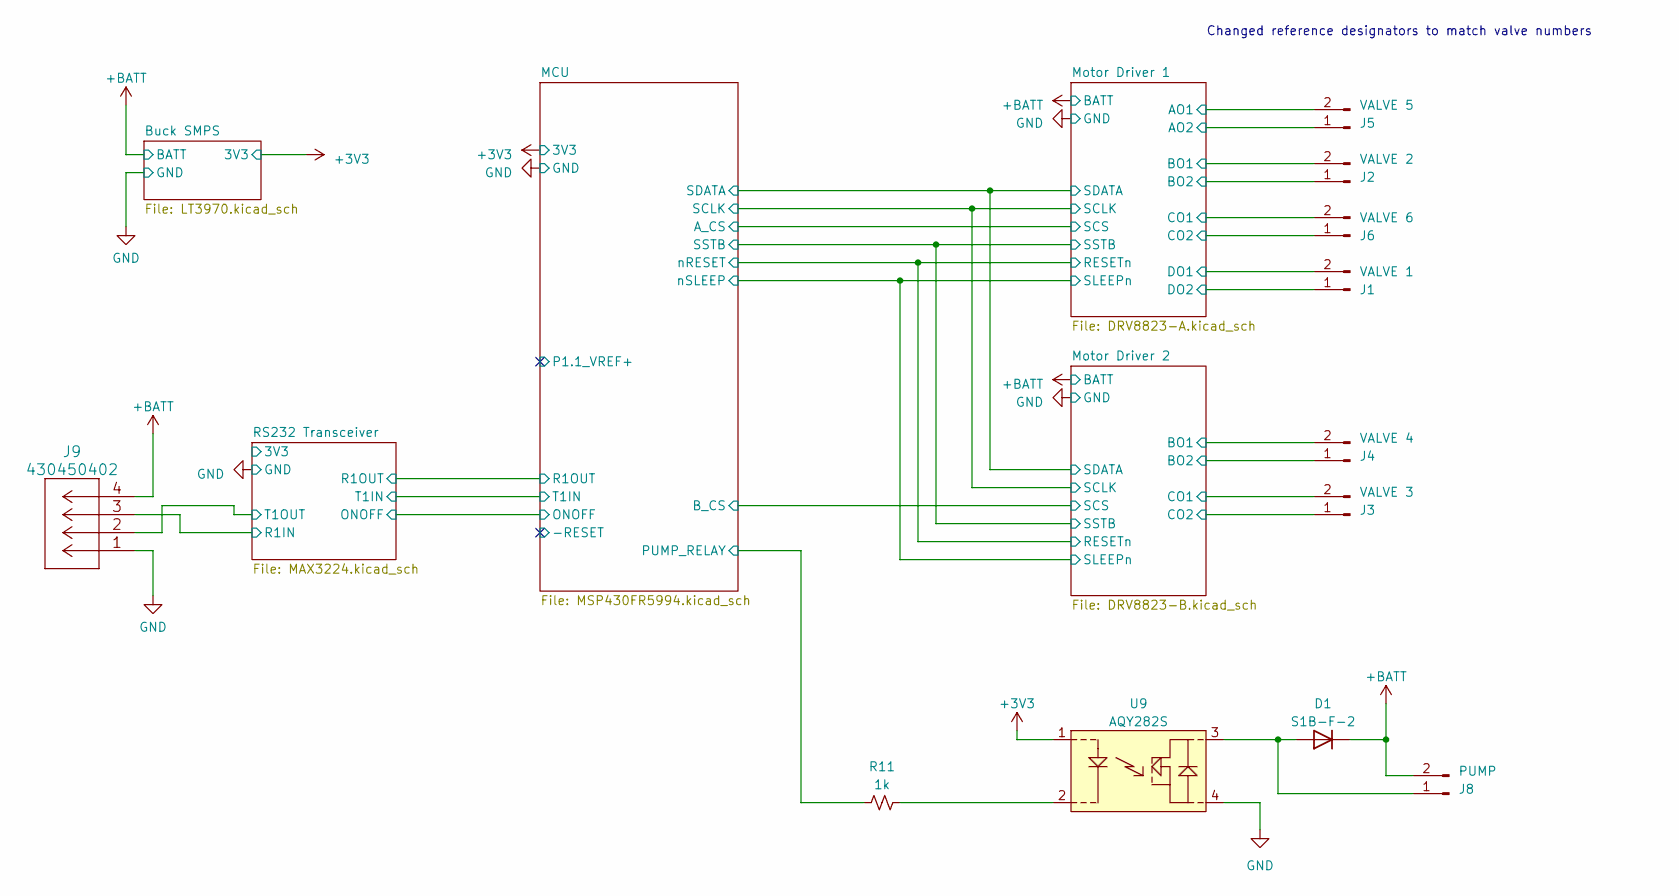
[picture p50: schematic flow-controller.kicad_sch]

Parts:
D1: S1B-F-2; D_SMA_Handsoldering; MPN S1B-13-F
J1: VALVE 1; PinHeader_1x02_P2.54mm_Vertical; MPN SSW-102-01-F-S
J2: VALVE 2; PinHeader_1x02_P2.54mm_Vertical; MPN SLW-102-01-F-S
J3: VALVE 3; PinHeader_1x02_P2.54mm_Vertical; MPN SSW-102-01-F-S
J4: VALVE 4; PinHeader_1x02_P2.54mm_Vertical; MPN SLW-102-01-F-S
J5: VALVE 5; PinHeader_1x02_P2.54mm_Vertical; MPN SSW-102-01-F-S
J6: VALVE 6; PinHeader_1x02_P2.54mm_Vertical; MPN SLW-102-01-F-S
J8: PUMP; 430450202; MPN 430450202
J9: 430450402; MPN 430450402
R11: 1k; R_0603_1608Metric_Pad0.98x0.95mm_HandSolder; MPN RT0603BRD071KL
U9: AQY282S; MPN AQY282S

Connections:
+3V3: U9.1; also elsewhere on the board
+BATT: D1.1 (K), J8.2, J9.4; also elsewhere on the board
/MCU/PUMP_RELAY: R11.1; also elsewhere on the board
/Motor Driver 1/AO1: J5.2; also elsewhere on the board
/Motor Driver 1/AO2: J5.1; also elsewhere on the board
/Motor Driver 1/BO1: J2.2; also elsewhere on the board
/Motor Driver 1/BO2: J2.1; also elsewhere on the board
/Motor Driver 1/CO1: J6.2; also elsewhere on the board
/Motor Driver 1/CO2: J6.1; also elsewhere on the board
/Motor Driver 1/DO1: J1.2; also elsewhere on the board
/Motor Driver 1/DO2: J1.1; also elsewhere on the board
/Motor Driver 2/BO1: J4.2; also elsewhere on the board
/Motor Driver 2/BO2: J4.1; also elsewhere on the board
/Motor Driver 2/CO1: J3.2; also elsewhere on the board
/Motor Driver 2/CO2: J3.1; also elsewhere on the board
/RS232 Transceiver/R1IN: J9.3; also elsewhere on the board
/RS232 Transceiver/T1OUT: J9.2; also elsewhere on the board
GND: J9.1, U9.4; also elsewhere on the board
unnamed: D1.2 (A), J8.1, U9.3
unnamed: R11.2, U9.2

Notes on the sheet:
Changed reference designators to match valve numbers

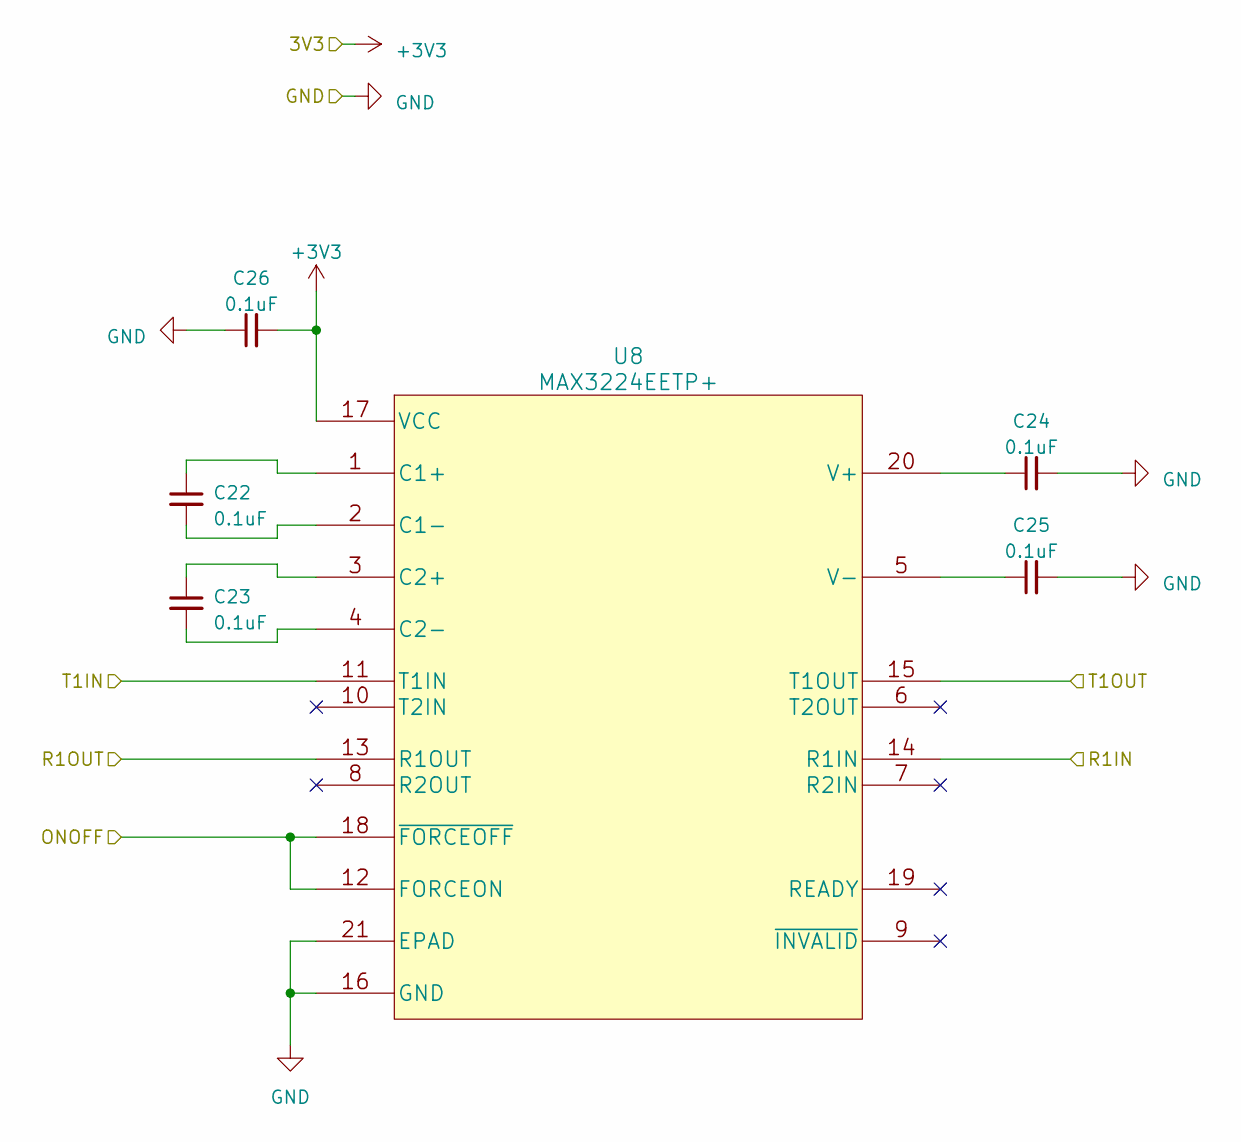
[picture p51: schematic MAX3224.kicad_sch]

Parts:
C22, C23, C24, C25, C26: 0.1uF; C_0603_1608Metric_Pad1.08x0.95mm_HandSolder; MPN C0603X104K5RAC7867
U8: MAX3224EETP+; MPN MAX3224EETP+

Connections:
+3V3: C26.2, U8.17 (VCC); also elsewhere on the board
/MCU/ONOFF: U8.12 (FORCEON), U8.18 (~FORCEOFF); also elsewhere on the board
/MCU/R1OUT: U8.13 (R1OUT); also elsewhere on the board
/MCU/T1IN: U8.11 (T1IN); also elsewhere on the board
/RS232 Transceiver/R1IN: U8.14 (R1IN); also elsewhere on the board
/RS232 Transceiver/T1OUT: U8.15 (T1OUT); also elsewhere on the board
GND: C24.2, C25.2, C26.1, U8.16 (GND), U8.21 (EPAD); also elsewhere on the board
unnamed: C22.1, U8.1 (C1+)
unnamed: C22.2, U8.2 (C1-)
unnamed: C23.1, U8.3 (C2+)
unnamed: C23.2, U8.4 (C2-)
unnamed: C24.1, U8.20 (V+)
unnamed: C25.1, U8.5 (V-)

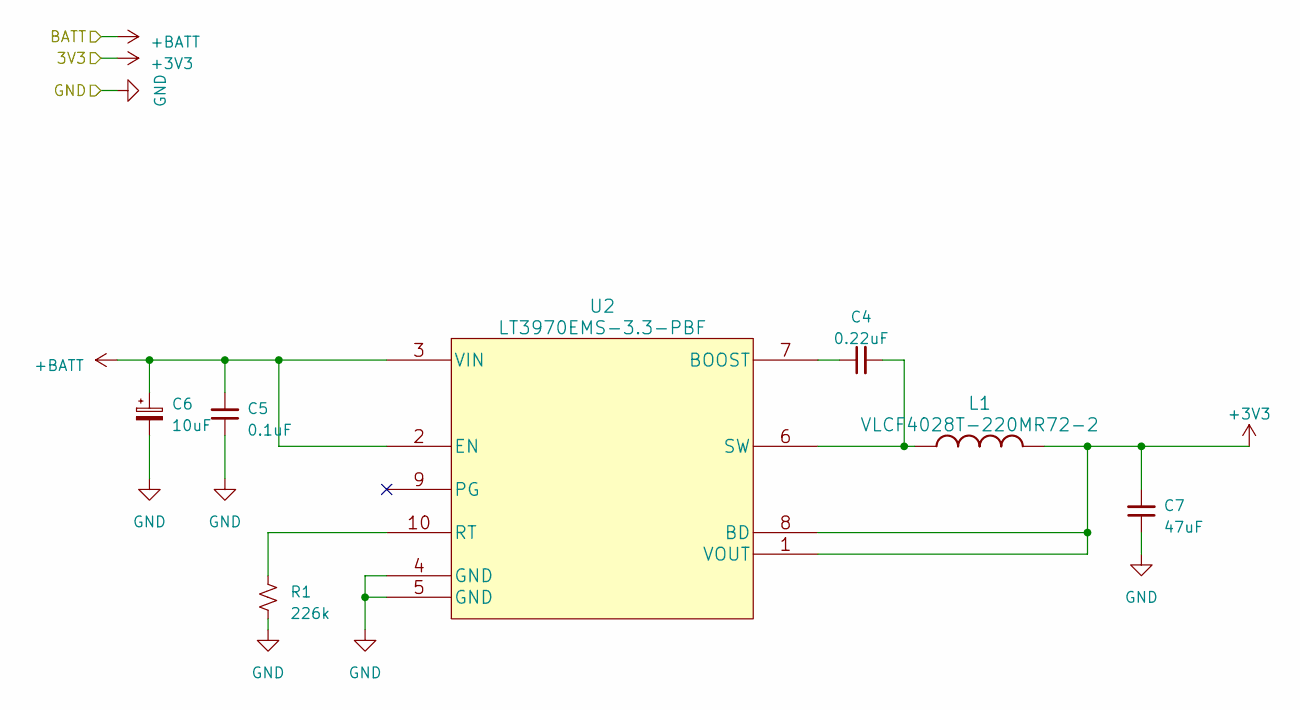
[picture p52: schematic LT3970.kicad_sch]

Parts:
C4: 0.22uF; C_0603_1608Metric_Pad1.08x0.95mm_HandSolder; MPN CGA3E3X7R1H224K080AB
C5: 0.1uF; C_0603_1608Metric_Pad1.08x0.95mm_HandSolder; MPN C0603X104K5RAC7867
C6: 10uF; C_1206_3216Metric_Pad1.33x1.80mm_HandSolder; MPN CGA5L1X7R1E106K160AE
C7: 47uF; C_1210_3225Metric_Pad1.33x2.70mm_HandSolder; MPN LMK325B7476MM-TR
L1: VLCF4028T-220MR72-2; MPN VLCF4028T-220MR72-2
R1: 226k; R_0603_1608Metric_Pad0.98x0.95mm_HandSolder; MPN ERJ-3EKF2263V
U2: LT3970EMS-3.3-PBF; MPN LT3970EMS-3.3-PBF

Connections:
+3V3: C7.2, L1.1, U2.1 (VOUT), U2.8 (BD); also elsewhere on the board
+BATT: C5.2, C6.1, U2.2 (EN), U2.3 (VIN); also elsewhere on the board
GND: C5.1, C6.2, C7.1, R1.2, U2.4 (GND), U2.5 (GND); also elsewhere on the board
unnamed: C4.1, U2.7 (BOOST)
unnamed: R1.1, U2.10 (RT)
unnamed: C4.2, L1.2, U2.6 (SW)

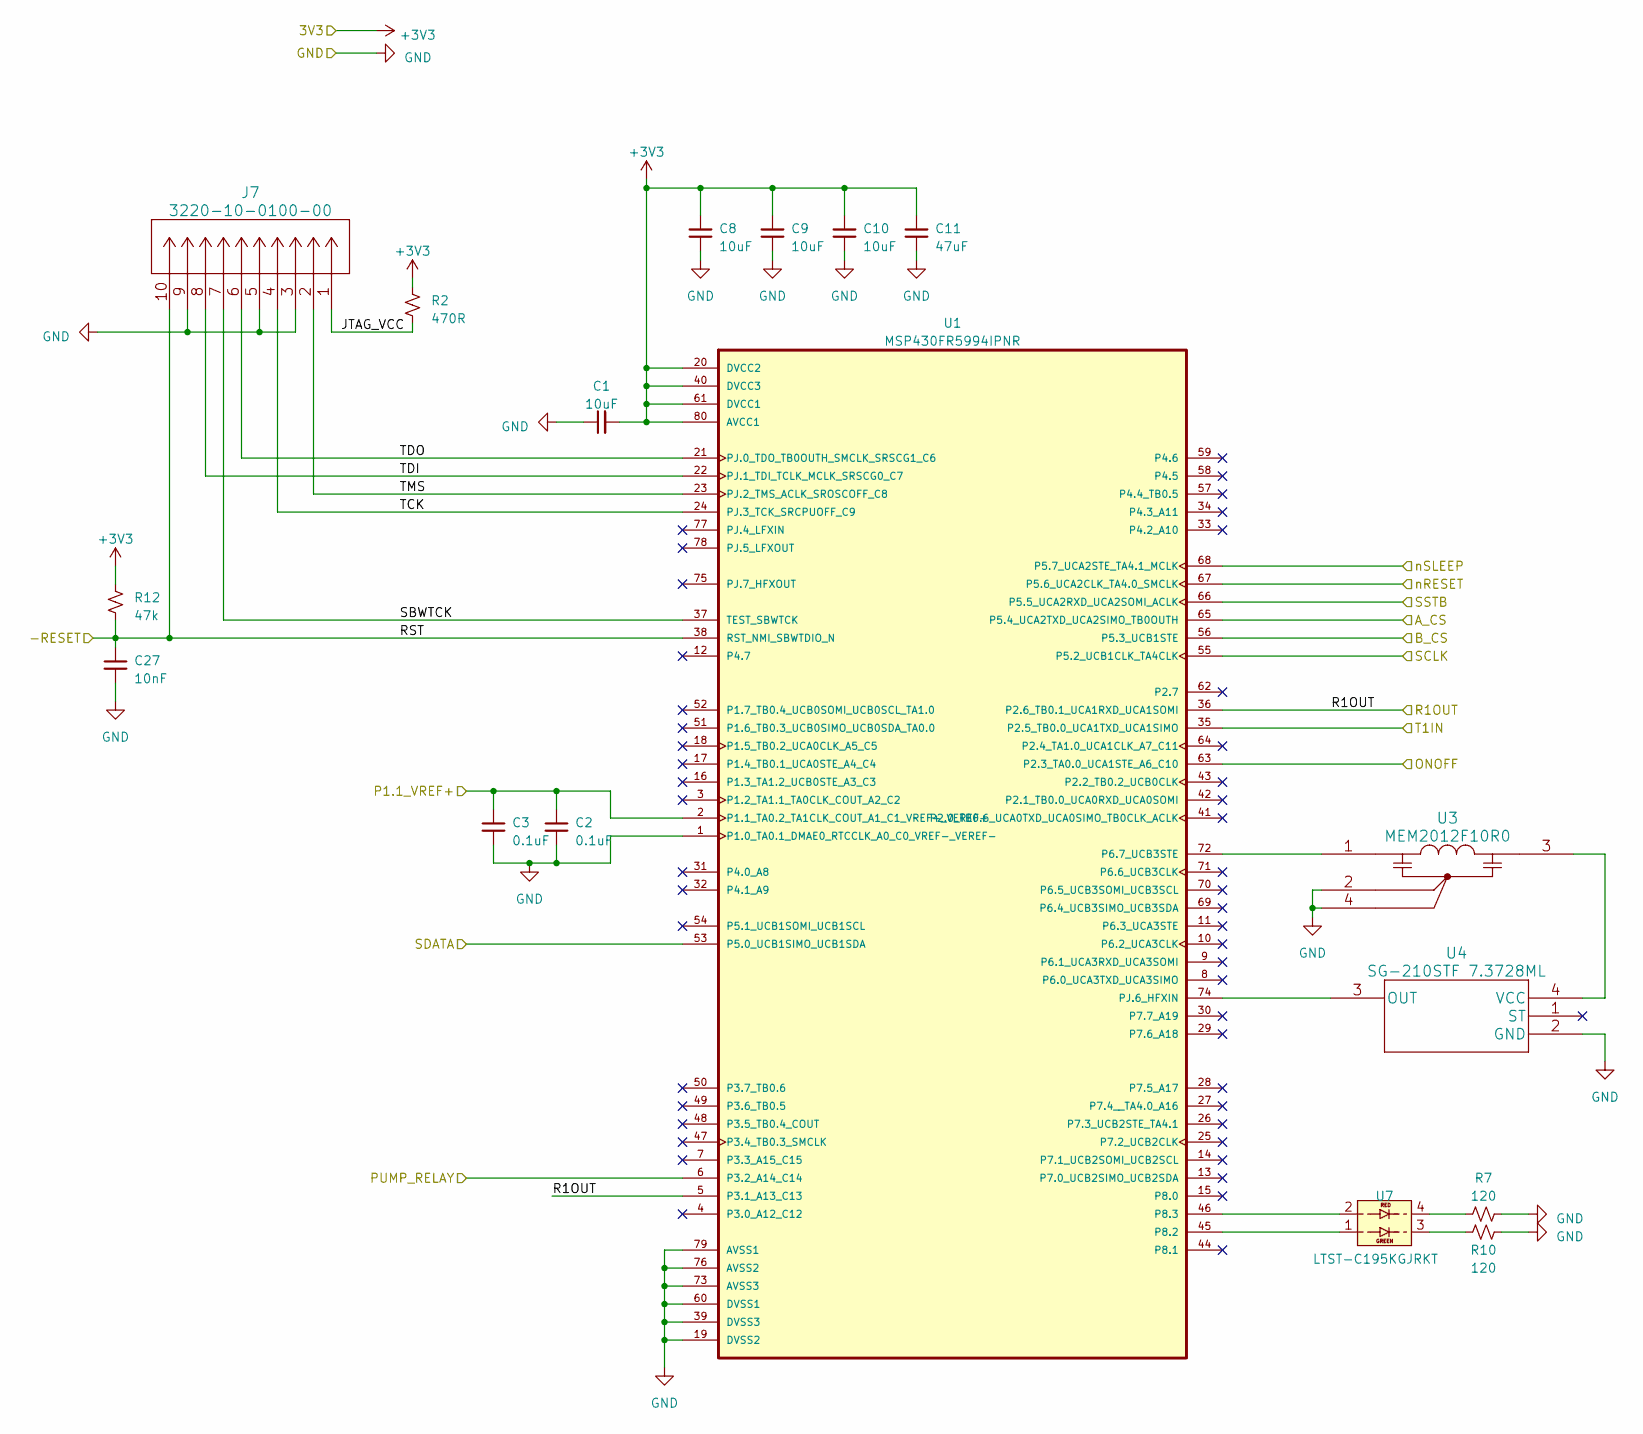
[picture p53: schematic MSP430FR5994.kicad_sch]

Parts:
C1, C8, C9, C10: 10uF; C_0603_1608Metric_Pad1.08x0.95mm_HandSolder; MPN CL10A106MQ8NNNC
C2, C3: 0.1uF; C_0603_1608Metric_Pad1.08x0.95mm_HandSolder; MPN C0603X104K5RAC7867
C11: 47uF; C_0603_1608Metric_Pad1.08x0.95mm_HandSolder; MPN 06033C473KAT2A
C27: 10nF; C_0603_1608Metric_Pad1.08x0.95mm_HandSolder; MPN C0603X103J4HAC7867
J7: 3220-10-0100-00; MPN 3220-10-0100-00
R2: 470R; R_0603_1608Metric_Pad0.98x0.95mm_HandSolder; MPN ESR03EZPJ471
R7, R10: 120; R_0603_1608Metric_Pad0.98x0.95mm_HandSolder; MPN ESR03EZPJ121
R12: 47k; R_0603_1608Metric_Pad0.98x0.95mm_HandSolder; MPN RC0603JR-1347KL
U1: MSP430FR5994IPNR; MPN MSP430FR5994IPNR
U3: MEM2012F10R0; MPN MEM2012F10R0
U4: SG-210STF 7.3728ML; MPN SG-210STF 7.3728ML
U7: LTST-C195KGJRKT; MPN LTST-C195KGJRKT

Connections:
+3V3: C1.2, C8.2, C9.2, C10.2, C11.2, R2.1, R12.1, U1.20 (DVCC2), U1.40 (DVCC3), U1.61 (DVCC1), U1.80 (AVCC1); also elsewhere on the board
/MCU/A_CS: U1.65 (P5.4_UCA2TXD_UCA2SIMO_TB0OUTH); also elsewhere on the board
/MCU/B_CS: U1.56 (P5.3_UCB1STE); also elsewhere on the board
/MCU/JTAG_VCC: J7.1, R2.2
/MCU/ONOFF: U1.63 (P2.3_TA0.0_UCA1STE_A6_C10); also elsewhere on the board
/MCU/P1.1_VREF+: C2.1, C3.1, U1.2 (P1.1_TA0.2_TA1CLK_COUT_A1_C1_VREF+_VERE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)
/MCU/PUMP_RELAY: U1.6 (P3.2_A14_C14); also elsewhere on the board
/MCU/R1OUT: U1.5 (P3.1_A13_C13), U1.36 (P2.6_TB0.1_UCA1RXD_UCA1SOMI); also elsewhere on the board
/MCU/RST: C27.1, J7.10, R12.2, U1.38 (RST_NMI_SBWTDIO_N)
/MCU/SBWTCK: J7.7, U1.37 (TEST_SBWTCK)
/MCU/SCLK: U1.55 (P5.2_UCB1CLK_TA4CLK); also elsewhere on the board
/MCU/SDATA: U1.53 (P5.0_UCB1SIMO_UCB1SDA); also elsewhere on the board
/MCU/SSTB: U1.66 (P5.5_UCA2RXD_UCA2SOMI_ACLK); also elsewhere on the board
/MCU/T1IN: U1.35 (P2.5_TB0.0_UCA1TXD_UCA1SIMO); also elsewhere on the board
/MCU/TCK: J7.4, U1.24 (PJ.3_TCK_SRCPUOFF_C9)
/MCU/TDI: J7.8, U1.22 (PJ.1_TDI_TCLK_MCLK_SRSCG0_C7)
/MCU/TDO: J7.6, U1.21 (PJ.0_TDO_TB0OUTH_SMCLK_SRSCG1_C6)
/MCU/TMS: J7.2, U1.23 (PJ.2_TMS_ACLK_SROSCOFF_C8)
/MCU/nRESET: U1.67 (P5.6_UCA2CLK_TA4.0_SMCLK); also elsewhere on the board
/MCU/nSLEEP: U1.68 (P5.7_UCA2STE_TA4.1_MCLK); also elsewhere on the board
GND: C1.1, C2.2, C3.2, C8.1, C9.1, C10.1, C11.1, C27.2, J7.3, J7.5, J7.9, R7.2, R10.2, U1.1 (P1.0_TA0.1_DMAE0_RTCCLK_A0_C0_VREF-_VER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), U1.19 (DVSS2), U1.39 (DVSS3), U1.60 (DVSS1), U1.73 (AVSS3), U1.76 (AVSS2), U1.79 (AVSS1), U3.2, U3.4, U4.2 (GND); also elsewhere on the board
unnamed: R7.1, U7.4
unnamed: R10.1, U7.3
unnamed: U1.72 (P6.7_UCB3STE), U3.1
unnamed: U1.45 (P8.2), U7.1
unnamed: U1.46 (P8.3), U7.2
unnamed: U1.74 (PJ.6_HFXIN), U4.3 (OUT)
unnamed: U3.3, U4.4 (VCC)

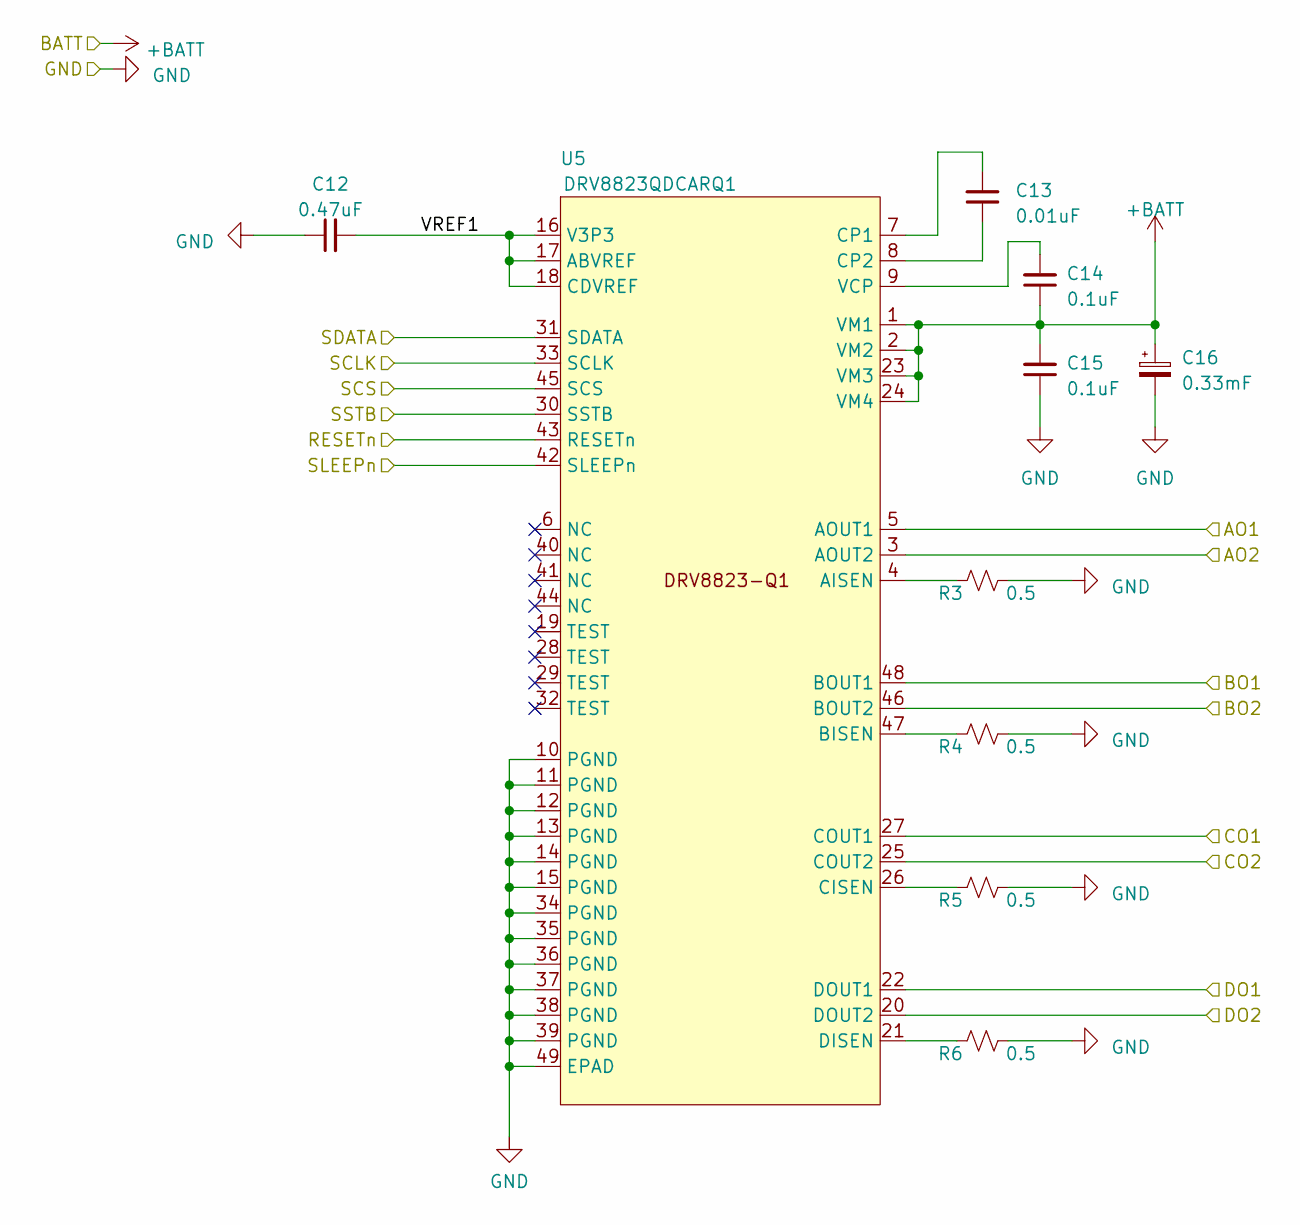
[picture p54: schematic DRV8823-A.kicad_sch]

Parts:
C12: 0.47uF; C_0603_1608Metric_Pad1.08x0.95mm_HandSolder; MPN CGA3E3X7R1H474K080AE
C13: 0.01uF; C_0603_1608Metric_Pad1.08x0.95mm_HandSolder; MPN C0603C103K2RACTU
C14, C15: 0.1uF; C_0603_1608Metric_Pad1.08x0.95mm_HandSolder; MPN C0603X104K5RAC7867
C16: 0.33mF; CP_Radial_D12.5mm_P5.00mm; MPN URZ1H331MHD1TO
R3, R4, R5, R6: 0.5; R_0603_1608Metric_Pad0.98x0.95mm_HandSolder; MPN RL0603FR-070R5L
U5: DRV8823QDCARQ1; HTSSOP48; MPN DRV8823QDCARQ1

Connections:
+BATT: C14.1, C15.2, C16.1, U5.1 (VM1), U5.2 (VM2), U5.23 (VM3), U5.24 (VM4); also elsewhere on the board
/MCU/A_CS: U5.45 (SCS); also elsewhere on the board
/MCU/SCLK: U5.33 (SCLK); also elsewhere on the board
/MCU/SDATA: U5.31 (SDATA); also elsewhere on the board
/MCU/SSTB: U5.30 (SSTB); also elsewhere on the board
/MCU/nRESET: U5.43 (RESETn); also elsewhere on the board
/MCU/nSLEEP: U5.42 (SLEEPn); also elsewhere on the board
/Motor Driver 1/AO1: U5.5 (AOUT1); also elsewhere on the board
/Motor Driver 1/AO2: U5.3 (AOUT2); also elsewhere on the board
/Motor Driver 1/BO1: U5.48 (BOUT1); also elsewhere on the board
/Motor Driver 1/BO2: U5.46 (BOUT2); also elsewhere on the board
/Motor Driver 1/CO1: U5.27 (COUT1); also elsewhere on the board
/Motor Driver 1/CO2: U5.25 (COUT2); also elsewhere on the board
/Motor Driver 1/DO1: U5.22 (DOUT1); also elsewhere on the board
/Motor Driver 1/DO2: U5.20 (DOUT2); also elsewhere on the board
/Motor Driver 1/VREF1: C12.2, U5.16 (V3P3), U5.17 (ABVREF), U5.18 (CDVREF)
GND: C12.1, C15.1, C16.2, R3.2, R4.2, R5.2, R6.2, U5.10 (PGND), U5.11 (PGND), U5.12 (PGND), U5.13 (PGND), U5.14 (PGND), U5.15 (PGND), U5.34 (PGND), U5.35 (PGND), U5.36 (PGND), U5.37 (PGND), U5.38 (PGND), U5.39 (PGND), U5.49 (EPAD); also elsewhere on the board
unnamed: R3.1, U5.4 (AISEN)
unnamed: R4.1, U5.47 (BISEN)
unnamed: R5.1, U5.26 (CISEN)
unnamed: C13.2, U5.7 (CP1)
unnamed: C13.1, U5.8 (CP2)
unnamed: R6.1, U5.21 (DISEN)
unnamed: C14.2, U5.9 (VCP)

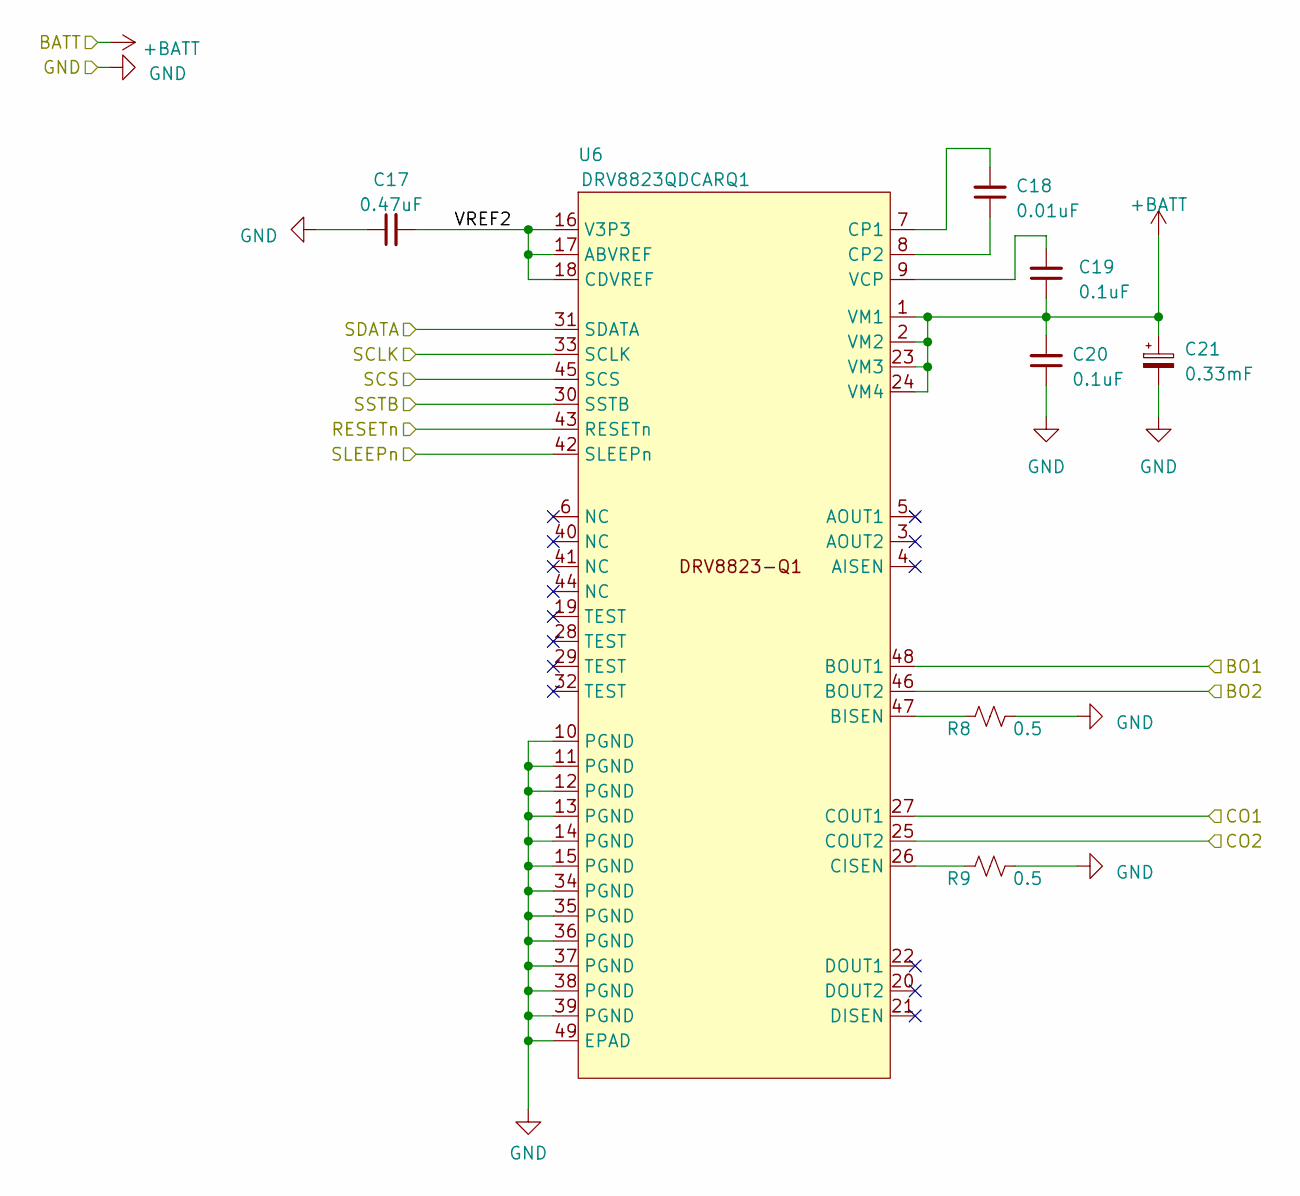
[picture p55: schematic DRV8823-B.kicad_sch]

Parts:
C17: 0.47uF; C_0603_1608Metric_Pad1.08x0.95mm_HandSolder; MPN CGA3E3X7R1H474K080AE
C18: 0.01uF; C_0603_1608Metric_Pad1.08x0.95mm_HandSolder; MPN C0603C103K2RACTU
C19, C20: 0.1uF; C_0603_1608Metric_Pad1.08x0.95mm_HandSolder; MPN C0603X104K5RAC7867
C21: 0.33mF; CP_Radial_D12.5mm_P5.00mm; MPN URZ1H331MHD1TO
R8, R9: 0.5; R_0603_1608Metric_Pad0.98x0.95mm_HandSolder; MPN RL0603FR-070R5L
U6: DRV8823QDCARQ1; HTSSOP48; MPN DRV8823QDCARQ1

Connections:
+BATT: C19.1, C20.2, C21.1, U6.1 (VM1), U6.2 (VM2), U6.23 (VM3), U6.24 (VM4); also elsewhere on the board
/MCU/B_CS: U6.45 (SCS); also elsewhere on the board
/MCU/SCLK: U6.33 (SCLK); also elsewhere on the board
/MCU/SDATA: U6.31 (SDATA); also elsewhere on the board
/MCU/SSTB: U6.30 (SSTB); also elsewhere on the board
/MCU/nRESET: U6.43 (RESETn); also elsewhere on the board
/MCU/nSLEEP: U6.42 (SLEEPn); also elsewhere on the board
/Motor Driver 2/BO1: U6.48 (BOUT1); also elsewhere on the board
/Motor Driver 2/BO2: U6.46 (BOUT2); also elsewhere on the board
/Motor Driver 2/CO1: U6.27 (COUT1); also elsewhere on the board
/Motor Driver 2/CO2: U6.25 (COUT2); also elsewhere on the board
/Motor Driver 2/VREF2: C17.2, U6.16 (V3P3), U6.17 (ABVREF), U6.18 (CDVREF)
GND: C17.1, C20.1, C21.2, R8.2, R9.2, U6.10 (PGND), U6.11 (PGND), U6.12 (PGND), U6.13 (PGND), U6.14 (PGND), U6.15 (PGND), U6.34 (PGND), U6.35 (PGND), U6.36 (PGND), U6.37 (PGND), U6.38 (PGND), U6.39 (PGND), U6.49 (EPAD); also elsewhere on the board
unnamed: R8.1, U6.47 (BISEN)
unnamed: R9.1, U6.26 (CISEN)
unnamed: C18.2, U6.7 (CP1)
unnamed: C18.1, U6.8 (CP2)
unnamed: C19.2, U6.9 (VCP)

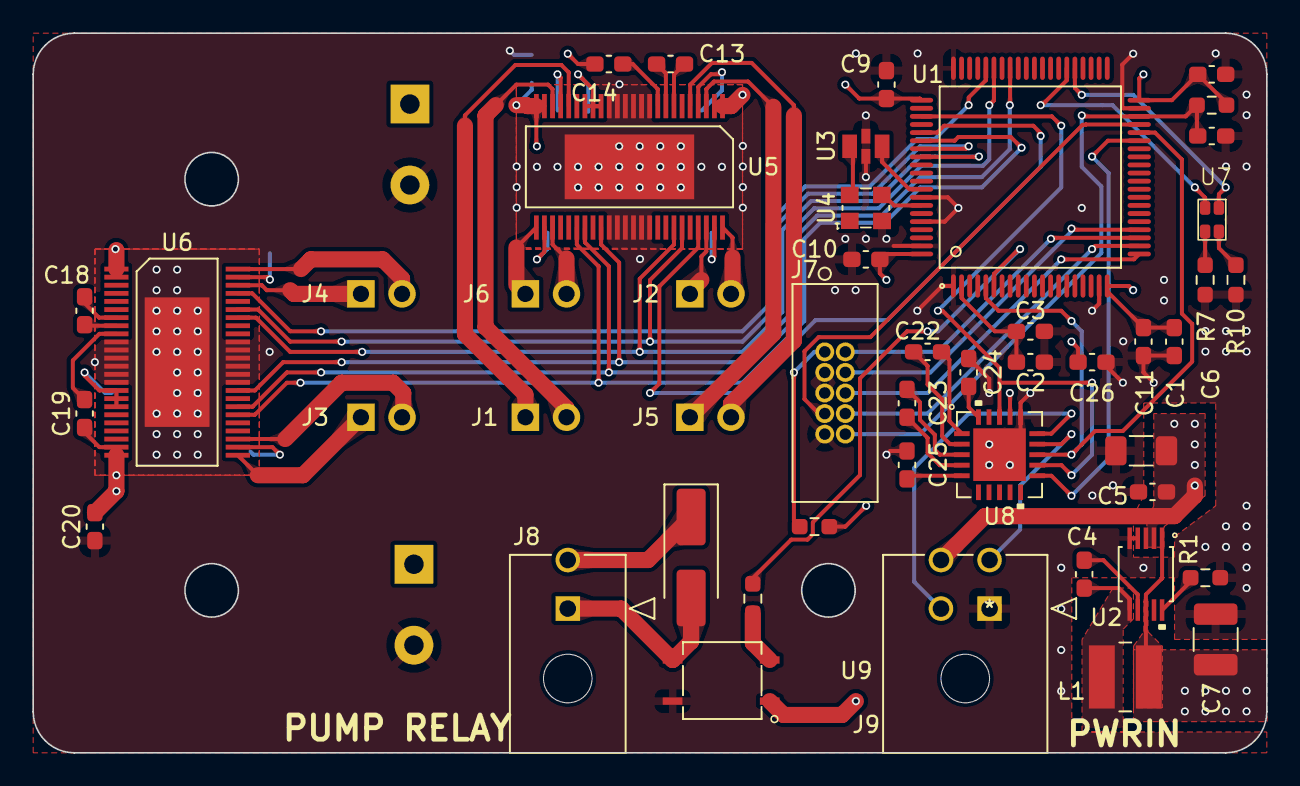
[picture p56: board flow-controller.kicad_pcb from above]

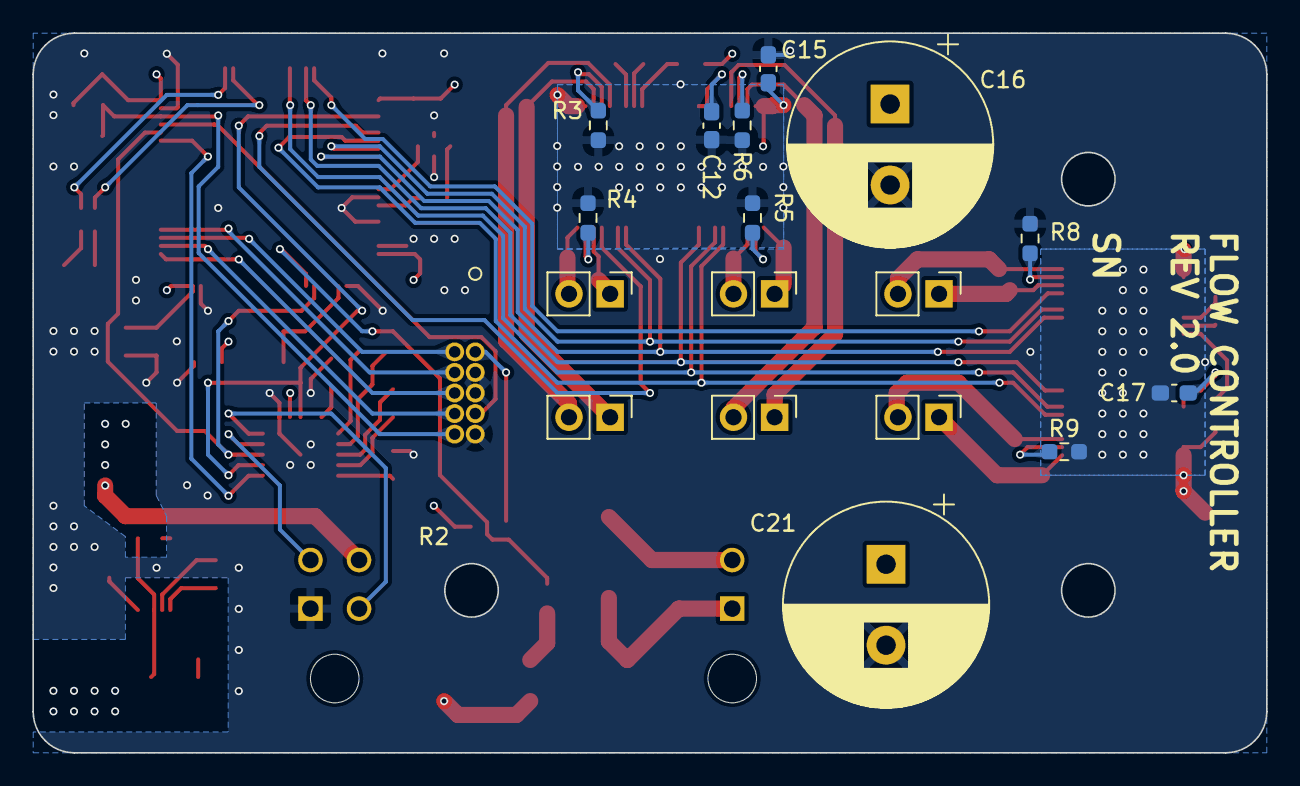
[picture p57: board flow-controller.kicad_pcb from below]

Board: 4 copper layers, 76.2 x 44.5 mm, 59 parts (17 on the bottom side), 68 nets.

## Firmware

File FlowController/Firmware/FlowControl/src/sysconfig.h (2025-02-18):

#ifndef _SYSCONFIG_H
#define _SYSCONFIG_H

#define SERIAL ("2017ABCDEFG")

/** EUSCI Ports */
#define PORT_A0 (0x01)
#define PORT_A1 (0x02)
#define PORT_A2 (0x04)
#define PORT_A3 (0x08)
#define PORT_B0 (0x10)
#define PORT_B1 (0x20)
#define PORT_B2 (0x40)
#define PORT_B3 (0x80)

/** ADC Channels */
#define ADC_0 (0x0001)
#define ADC_1 (0x0002)
#define ADC_2 (0x0004)
#define ADC_3 (0x0008)
#define ADC_4 (0x0010)
#define ADC_5 (0x0020)
#define ADC_6 (0x0040)
#define ADC_7 (0x0080)
#define ADC_8 (0x0100)
#define ADC_9 (0x0200)
#define ADC_10 (0x0400)
#define ADC_11 (0x0800)
#define ADC_12 (0x1000)

/** Crystal Frequencies */
#define HFXT_FREQ (7327800)
#define HFXT_DRIVE (HFXTDRIVE_2)
#define HFXT_TIMEOUT (HFXT_FREQ / 10)

#define LFXT_FREQ (0u)
#define LFXT_DRIVE (LFXTDRIVE_2)
#define LFXT_TIMEOUT (LFXT_FREQ)

/** System Clock Frequencies, Sources and Dividers */
#define MCLK_DIV (CS_CLOCK_DIVIDER_2)
#define MCLK_SRC (CS_HFXTCLK_SELECT) //(SELM__HFXTCLK)
#define MCLK_FREQ (HFXT_FREQ / 2)
#define MCLK_DRIVE (HFXTDRIVE_2)

#define SMCLK_DIV (CS_CLOCK_DIVIDER_8)
#define SMCLK_SRC (CS_HFXTCLK_SELECT) //(SELM__HFXTCLK)
#define SMCLK_FREQ (HFXT_FREQ / 8)

#define ACLK_DIV (CS_CLOCK_DIVIDER_16)
#define ACLK_SRC (CS_VLOCLK_SELECT) //(SELM__HFXTCLK)
#define ACLK_FREQ (10000)

#define MODOSC_DIV (32)
#define MODOSC_SRC (SELM__HFXTCLK)
#define MODOSC_FREQ (HFXT_FREQ / 32)

/** Initialization Delay */
#define SYS_BOARD_INIT_DELAY (100)

/** System Timer Settings */
#define SYS_TIMER_A_BASE_ADDRESS (TA0_BASE)
#define SYS_TIMER_A_CLOCKSOURCE (TIMER_A_CLOCKSOURCE_ACLK)
#define SYS_TIMER_A_CLOCK_DIVIDER (TIMER_A_CLOCKSOURCE_DIVIDER_1)
#define SYS_TIMER_A_TIE (TIMER_A_TAIE_INTERRUPT_ENABLE)
#define SYS_TIMER_A_COMPARE (TIMER_A_CCIE_CCR0_INTERRUPT_DISABLE)
#define SYS_TIMER_A_CLEAR (TIMER_A_DO_CLEAR)
#define SYS_TIMER_A_FREQUENCY (10000)
#define SYS_TIMER_A_PERIOD (SYS_TIMER_A_FREQUENCY / 1000) /** 1kHz */

#define SYS_TIMER_B_BASE_ADDRESS (TB0_BASE)
#define SYS_TIMER_B_CLOCKSOURCE (TIMER_B_CLOCKSOURCE_ACLK)
#define SYS_TIMER_B_CLOCK_DIVIDER (TIMER_B_CLOCKSOURCE_DIVIDER_8)
#define SYS_TIMER_B_TIE (TIMER_B_TBIE_INTERRUPT_ENABLE)
#define SYS_TIMER_B_COMPARE (TIMER_B_CCIE_CCR0_INTERRUPT_DISABLE)
#define SYS_TIMER_B_CLEAR (TIMER_B_DO_CLEAR)
#define SYS_TIMER_B_FREQUENCY (10000)
#define SYS_TIMER_B_PERIOD (SYS_TIMER_B_FREQUENCY / 5) /** 5Hz */

/** UART VALUES */
#define UART_ACK (0x06)
#define UART_NACK (0x15)
#define UART_ENDLINE ("\r\n")

#define UART_A1_TX_PORT (GPIO_PORT_P2)
#define UART_A1_TX_PIN (GPIO_PIN5)
#define UART_A1_RX_PORT (GPIO_PORT_P2)
#define UART_A1_RX_PIN (GPIO_PIN6)
/** GPIO Pin Direction */
#define PIN_OUT (0)
#define PIN_IN (1)

/** GPIO PIN XOR */
#define PIN_POLARITY_NORMAL (0)
#define PIN_POLARITY_REVERSE (1)

#define SYS_UART_BUFFER_LEN (80)

/** Console configurations */
#define SYS_CONSOLE_UART_PORT (EUSCI_A0_BASE)
#define SYS_CONSOLE_UART_CLK (UCSSEL__SMCLK)
#define SYS_CONSOLE_UART_CLK_FREQ (SMCLK_FREQ)
#define SYS_CONSOLE_UART_BAUDRATE (115200)
#define SYS_CONSOLE_PORT_CONFIG1() (P2SEL1 |= (BIT0 | BIT1))
#define SYS_CONSOLE_PORT_CONFIG0() (P2SEL0 &= ~(BIT0 | BIT1))
#define SYS_CONSOLE_UART_PARITY (EUSCI_A_UART_EVEN_PARITY)
#define SYS_CONSOLE_UART_MSB_FIRST (EUSCI_A_UART_LSB_FIRST)
#define SYS_CONSOLE_UART_STOPBITS (EUSCI_A_UART_ONE_STOP_BIT)
#define SYS_CONSOLE_UART_MODE (EUSCI_A_UART_MODE)

/** Command configurations */
#define SYS_COMMAND_UART_PORT (EUSCI_A1_BASE)
#define SYS_COMMAND_UART_CLK (UCSSEL__SMCLK)
#define SYS_COMMAND_UART_CLK_FREQ (SMCLK_FREQ)
#define SYS_COMMAND_UART_BAUDRATE (9600)
#define SYS_COMMAND_PORT_CONFIG1() (P2SEL1 |= (BIT5 | BIT6))
#define SYS_COMMAND_PORT_CONFIG0() (P2SEL0 &= ~(BIT5 | BIT6))
#define SYS_COMMAND_UART_PARITY (EUSCI_A_UART_EVEN_PARITY)
#define SYS_COMMAND_UART_MSB_FIRST (EUSCI_A_UART_LSB_FIRST)
#define SYS_COMMAND_UART_STOPBITS (EUSCI_A_UART_ONE_STOP_BIT)
#define SYS_COMMAND_UART_MODE (EUSCI_A_UART_MODE)

/** Relay Configurations */
#define SYS_RELAY_TOGGLE_PORT (GPIO_PORT_P3)
#define SYS_RELAY_TOGGLE_PIN (GPIO_PIN2)
#define SYS_RELAY_TOGGLE_DIR (PIN_OUT)
#define SYS_RELAY_TOGGLE_POL (PIN_POLARITY_REVERSE)

/** HBridge (DRV8823) Configurations */
#define SYS_MCONTROL_NSLEEP_PORT (GPIO_PORT_P5)
#define SYS_MCONTROL_NSLEEP_PIN (GPIO_PIN7)
#define SYS_MCONTROL_NSLEEP_DIR (PIN_OUT)
#define SYS_MCONTROL_NSLEEP_POL (PIN_POLARITY_NORMAL)

#define SYS_MCONTROL_NRESET_PORT (GPIO_PORT_P5)
#define SYS_MCONTROL_NRESET_PIN (GPIO_PIN6)
#define SYS_MCONTROL_NRESET_DIR (PIN_OUT)
#define SYS_MCONTROL_NRESET_POL (PIN_POLARITY_NORMAL)

#define SYS_MCONTROL_STROBE_PORT (GPIO_PORT_P5)
#define SYS_MCONTROL_STROBE_PIN (GPIO_PIN5)
#define SYS_MCONTROL_STROBE_DIR (PIN_OUT)
#define SYS_MCONTROL_STROBE_POL (PIN_POLARITY_NORMAL)

#define SYS_MCONTROL_BRIDGE_A_SPI_BASE (EUSCI_B1_BASE)
#define SYS_MCONTROL_BRIDGE_A_CS_PORT (GPIO_PORT_P5)
#define SYS_MCONTROL_BRIDGE_A_CS_PIN (GPIO_PIN4)
#define SYS_MCONTROL_BRIDGE_A_CS_DIR (PIN_OUT)
#define SYS_MCONTROL_BRIDGE_A_CS_POL (PIN_POLARITY_NORMAL)

#define SYS_MCONTROL_BRIDGE_B_SPI_BASE (EUSCI_B1_BASE)
#define SYS_MCONTROL_BRIDGE_B_CS_PORT (GPIO_PORT_P5)
#define SYS_MCONTROL_BRIDGE_B_CS_PIN (GPIO_PIN3)
#define SYS_MCONTROL_BRIDGE_B_CS_DIR (PIN_OUT)
#define SYS_MCONTROL_BRIDGE_B_CS_POL (PIN_POLARITY_NORMAL)

#define SYS_MCONTROL_SPI_CHANNEL (SPI_B1) /** Port B1 */
#define SYS_MCONTROL_SPI_BAUD (100000)
#define SYS_MCONTROL_SPI_CLK (SMCLK)
#define SYS_MCONTROL_SPI_CLK_FREQ (SMCLK_FREQ)
#define SYS_MCONTROL_SPI_MSBFIRST (EUSCI_B_SPI_LSB_FIRST)
#define SYS_MCONTROL_SPI_CLK_PHASE (EUSCI_B_SPI_PHASE_DATA_CHANGED_ONFIRST_CAPTURED_ON_NEXT)
#define SYS_MCONTROL_SPI_CLK_POL (EUSCI_B_SPI_CLOCKPOLARITY_INACTIVITY_LOW)
#define SYS_MCONTROL_SPI_MODE (EUSCI_B_SPI_3PIN)

#define SPI_B1_CLK_PORT (GPIO_PORT_P5)
#define SPI_B1_CLK_PIN (GPIO_PIN2)
#define SPI_B1_SIMO_PORT (GPIO_PORT_P5)
#define SPI_B1_SIMO_PIN (GPIO_PIN0)
#define SPI_B1_SOMI_PORT (GPIO_PORT_P5)
#define SPI_B1_SOMI_PIN (GPIO_PIN1)

#define SYS_MCONTROL_PORT_CONFIG1() (P5SEL1 &= ~(BIT0))
#define SYS_MCONTROL_PORT_CONFIG0() (P5SEL0 |= (BIT0))

#define SYS_DRV8823_STROBE_DELAY_MS (1)
#define SYS_DRV8823_RESET_DELAY_MS (50)
#define SYS_DRV8823_WAKEUP_DELAY_MS (3)

/** Ambiq RTC Configurations */
#define SYS_AMBIQ_I2C_CHANNEL (PORT_B0)
#define SYS_AMBIQ_I2C_BAUD (200000)
#define SYS_AMBIQ_I2C_CLK (SMCLK)
#define SYS_AMBIQ_I2C_CLK_FREQ (SMCLK_FREQ)

#define SYS_AMBIQ_NIRQ1_PORT (1)
#define SYS_AMBIQ_NIRQ1_PIN (4)
#define SYS_AMBIQ_NIRQ1_DIR (PIN_IN)
#define SYS_AMBIQ_NIRQ1_POL (PIN_POLARITY_REVERSE)

#define SYS_AMBIQ_NIRQ2_PORT (1)
#define SYS_AMBIQ_NIRQ2_PIN (5)
#define SYS_AMBIQ_NIRQ2_DIR (PIN_IN)
#define SYS_AMBIQ_NIRQ2_POL (PIN_POLARITY_REVERSE)

#define SYS_AMBIQ_EXTI_PORT (1)
#define SYS_AMBIQ_EXTI_PIN (3)
#define SYS_AMBIQ_EXTI_DIR (PIN_IN)
#define SYS_AMBIQ_EXTI_POL (PIN_POLARITY_NORMAL)

#define SYS_AMBIQ_NTIRQ_PORT (1)
#define SYS_AMBIQ_NTIRQ_PIN (2)
#define SYS_AMBIQ_NTIRQ_DIR (PIN_IN)
#define SYS_AMBIQ_NTIRQ_POL ()

/** Watchdog Configuration */
#define SYS_WD_PORT (4)
#define SYS_WD_PIN (7)
#define SYS_WD_DIR (PIN_OUT)
#define SYS_WD_POL (PIN_POLARITY_NORMAL)

/** LED Configuration */
#define SYS_LED_GREEN_PORT (GPIO_PORT_P8)
#define SYS_LED_GREEN_PIN (GPIO_PIN2)
#define SYS_LED_GREEN_DIR (PIN_OUT)
#define SYS_LED_GREEN_POL (PIN_POLARITY_NORMAL)

#define SYS_LED_RED_PORT (GPIO_PORT_P8)
#define SYS_LED_RED_PIN (GPIO_PIN3)
#define SYS_LED_RED_DIR (PIN_OUT)
#define SYS_LED_RED_POL (PIN_POLARITY_NORMAL)

/** Analog Configuration */
#define SYS_ANALOG_CHAN1 (ADC_8)
#define SYS_ANALOG_CHAN2 (ADC_9)
#define SYS_ANALOG_CHAN3 (ADC_10)
#define SYS_ANALOG_CHAN4 (ADC_11)

/** Motion Control Valve State Settings */
#define MOTION_VALVE_PULSE_DELAY_MINIMUM (15)
#define MOTION_VALVE_WAKEUP (10)
#define MOTION_VALVE_PULSE_DELAY (50) /** 50ms Pulse */
#define MOTION_VALVE_CA (1)
#define MOTION_VALVE_CB (0)
#define MOTION_VALVE_NOM_CURRENT (4)
#define MOTION_VALVE_DECAY (0)

#define MOTION_VALVE_1_BRIDGE (DRV_A)
#define MOTION_VALVE_1_CHAN (DRV8823_CHAN_D)
#define MOTION_VALVE_2_BRIDGE (DRV_A)
#define MOTION_VALVE_2_CHAN (DRV8823_CHAN_B)
#define MOTION_VALVE_3_BRIDGE (DRV_B)
#define MOTION_VALVE_3_CHAN (DRV8823_CHAN_C)
#define MOTION_VALVE_4_BRIDGE (DRV_B)
#define MOTION_VALVE_4_CHAN (DRV8823_CHAN_B)
#define MOTION_VALVE_5_BRIDGE (DRV_A)
#define MOTION_VALVE_5_CHAN (DRV8823_CHAN_A)
#define MOTION_VALVE_6_BRIDGE (DRV_A)
#define MOTION_VALVE_6_CHAN (DRV8823_CHAN_C)
#define MOTION_VALVE_7_BRIDGE (DRV_B)
#define MOTION_VALVE_7_CHAN (DRV8823_CHAN_A)
#define MOTION_VALVE_8_BRIDGE (DRV_B)
#define MOTION_VALVE_8_CHAN (DRV8823_CHAN_D)

#define MOTION_ZERO_PUMP_DIR_V1 (MOTION_VALVE_CB)
#define MOTION_ZERO_PUMP_DIR_V2 (MOTION_VALVE_CB)
#define MOTION_ZERO_PUMP_DIR_V3 (MOTION_VALVE_CB)
#define MOTION_ZERO_PUMP_DIR_V4 (MOTION_VALVE_CB)
#define MOTION_ZERO_PUMP_DIR_V5 (MOTION_VALVE_CA)
#define MOTION_ZERO_PUMP_DIR_V6 (MOTION_VALVE_CB)
#define MOTION_ZERO_PUMP_DIR_V7 (MOTION_VALVE_CB)
#define MOTION_ZERO_PUMP_DIR_V8 (MOTION_VALVE_CB)

#define MOTION_ZERO_VENT_DIR_V1 (MOTION_VALVE_CB)
#define MOTION_ZERO_VENT_DIR_V2 (MOTION_VALVE_CB)
#define MOTION_ZERO_VENT_DIR_V3 (MOTION_VALVE_CB)
#define MOTION_ZERO_VENT_DIR_V4 (MOTION_VALVE_CA)
#define MOTION_ZERO_VENT_DIR_V5 (MOTION_VALVE_CA)
#define MOTION_ZERO_VENT_DIR_V6 (MOTION_VALVE_CB)
#define MOTION_ZERO_VENT_DIR_V7 (MOTION_VALVE_CB)
#define MOTION_ZERO_VENT_DIR_V8 (MOTION_VALVE_CB)

#define MOTION_ZERO_CAL_DIR_V1 (MOTION_VALVE_CB)
#define MOTION_ZERO_CAL_DIR_V2 (MOTION_VALVE_CB)
#define MOTION_ZERO_CAL_DIR_V3 (MOTION_VALVE_CB)
#define MOTION_ZERO_CAL_DIR_V4 (MOTION_VALVE_CB)
#define MOTION_ZERO_CAL_DIR_V5 (MOTION_VALVE_CA)
#define MOTION_ZERO_CAL_DIR_V6 (MOTION_VALVE_CB)
#define MOTION_ZERO_CAL_DIR_V7 (MOTION_VALVE_CB)
#define MOTION_ZERO_CAL_DIR_V8 (MOTION_VALVE_CB)

#define MOTION_SPAN_PUMP_DIR_V1 (MOTION_VALVE_CA)
#define MOTION_SPAN_PUMP_DIR_V2 (MOTION_VALVE_CB)
#define MOTION_SPAN_PUMP_DIR_V3 (MOTION_VALVE_CB)
#define MOTION_SPAN_PUMP_DIR_V4 (MOTION_VALVE_CA)
#define MOTION_SPAN_PUMP_DIR_V5 (MOTION_VALVE_CB)
#define MOTION_SPAN_PUMP_DIR_V6 (MOTION_VALVE_CA)
#define MOTION_SPAN_PUMP_DIR_V7 (MOTION_VALVE_CB)
#define MOTION_SPAN_PUMP_DIR_V8 (MOTION_VALVE_CB)

#define MOTION_SPAN_VENT_DIR_V1 (MOTION_VALVE_CA)
#define MOTION_SPAN_VENT_DIR_V2 (MOTION_VALVE_CB)
#define MOTION_SPAN_VENT_DIR_V3 (MOTION_VALVE_CB)
#define MOTION_SPAN_VENT_DIR_V4 (MOTION_VALVE_CA)
#define MOTION_SPAN_VENT_DIR_V5 (MOTION_VALVE_CA)
#define MOTION_SPAN_VENT_DIR_V6 (MOTION_VALVE_CA)
#define MOTION_SPAN_VENT_DIR_V7 (MOTION_VALVE_CB)
#define MOTION_SPAN_VENT_DIR_V8 (MOTION_VALVE_CB)

#define MOTION_SPAN_CAL_DIR_V1 (MOTION_VALVE_CA)
#define MOTION_SPAN_CAL_DIR_V2 (MOTION_VALVE_CB)
#define MOTION_SPAN_CAL_DIR_V3 (MOTION_VALVE_CB)
#define MOTION_SPAN_CAL_DIR_V4 (MOTION_VALVE_CB)
#define MOTION_SPAN_CAL_DIR_V5 (MOTION_VALVE_CA)
#define MOTION_SPAN_CAL_DIR_V6 (MOTION_VALVE_CB)
#define MOTION_SPAN_CAL_DIR_V7 (MOTION_VALVE_CB)
#define MOTION_SPAN_CAL_DIR_V8 (MOTION_VALVE_CB)

#define MOTION_EQUIL_PUMP_DIR_V1 (MOTION_VALVE_CB)
#define MOTION_EQUIL_PUMP_DIR_V2 (MOTION_VALVE_CA)
#define MOTION_EQUIL_PUMP_DIR_V3 (MOTION_VALVE_CA)
#define MOTION_EQUIL_PUMP_DIR_V4 (MOTION_VALVE_CB)
#define MOTION_EQUIL_PUMP_DIR_V5 (MOTION_VALVE_CA)
#define MOTION_EQUIL_PUMP_DIR_V6 (MOTION_VALVE_CA)
#define MOTION_EQUIL_PUMP_DIR_V7 (MOTION_VALVE_CB)
#define MOTION_EQUIL_PUMP_DIR_V8 (MOTION_VALVE_CB)

#define MOTION_EQUIL_VENT_DIR_V1 (MOTION_VALVE_CA)
#define MOTION_EQUIL_VENT_DIR_V2 (MOTION_VALVE_CB)
#define MOTION_EQUIL_VENT_DIR_V3 (MOTION_VALVE_CB)
#define MOTION_EQUIL_VENT_DIR_V4 (MOTION_VALVE_CA)
#define MOTION_EQUIL_VENT_DIR_V5 (MOTION_VALVE_CA)
#define MOTION_EQUIL_VENT_DIR_V6 (MOTION_VALVE_CA)
#define MOTION_EQUIL_VENT_DIR_V7 (MOTION_VALVE_CB)
#define MOTION_EQUIL_VENT_DIR_V8 (MOTION_VALVE_CB)
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

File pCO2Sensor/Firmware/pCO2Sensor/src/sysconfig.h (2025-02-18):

#ifndef _SYSCONFIG_H
#define _SYSCONFIG_H

/************************************************************************
 *		        User Settings
 ************************************************************************/
/** User Settable */

/** Board Version */
//#define BOARD_VER_1_0         /**< Uncomment for PCB Version 1.0 */
//#define BOARD_VER_1_1         /**< Uncomment for PCB Version 1.1 */
#define BOARD_VER_1_3_2 /**< Uncomment for PCB Version 1.3.2 */

/** Test Cycle Settings */
#define TEST_RTC /**< Uncomment for Testing RTC Output */
//#define TEST_NO_RUN           /**< Uncomment to prevent run during alarm */
#define TEST_QUICK_PERIODS    /**< Uncomment to reduce the length of time of run */

/** Initialization Delay */
#define SYS_BOARD_INIT_DELAY (100) /** Startup delay (ms) */

/** Console Buffer Receive Length */
#define SYSTEM_CONSOLE_RX_BUFFER_LEN (128) /** Length of Console buffer */
#define SYSTEM_CONSOLE_RX_TIMEOUT (1500)   /** Console receive timeout (ms) */

/** Command Buffer Receive Length */
#define SYSTEM_COMMAND_RX_BUFFER_LEN (256) /** Length of Command buffer */
#define SYSTEM_COMMAND_RX_TIMEOUT (50)     /** Command receive timeout (ms) */

/** Default time settings.  Change to integer numbers to alter defaults */
#ifdef TEST_QUICK_PERIODS
#define DEFAULT_PCO2_NORM_START_YEAR (0)
#define DEFAULT_PCO2_NORM_START_MONTH (0)
#define DEFAULT_PCO2_NORM_START_DATE (0)
#define DEFAULT_PCO2_NORM_START_HOUR (0)
#define DEFAULT_PCO2_NORM_START_MINUTE (0)
#define DEFAULT_PCO2_NORM_START_SECOND (0)
#define DEFAULT_PCO2_NORM_INTERVAL_YEAR (0)
#define DEFAULT_PCO2_NORM_INTERVAL_MONTH (0)
#define DEFAULT_PCO2_NORM_INTERVAL_DATE (0)
#define DEFAULT_PCO2_NORM_INTERVAL_HOUR (0)
#define DEFAULT_PCO2_NORM_INTERVAL_MINUTE (10)
#define DEFAULT_PCO2_NORM_INTERVAL_SECOND (0)
#define DEFAULT_PCO2_FAST_INTERVAL_YEAR (0)
#define DEFAULT_PCO2_FAST_INTERVAL_MONTH (0)
#define DEFAULT_PCO2_FAST_INTERVAL_DATE (0)
#define DEFAULT_PCO2_FAST_INTERVAL_HOUR (0)
#define DEFAULT_PCO2_FAST_INTERVAL_MINUTE (4)
#define DEFAULT_PCO2_FAST_INTERVAL_SECOND (0)
#define DEFAULT_PCO2_FAST_CHANGE_YEAR (0)
#define DEFAULT_PCO2_FAST_CHANGE_MONTH (0)
#define DEFAULT_PCO2_FAST_CHANGE_DATE (0)
#define DEFAULT_PCO2_FAST_CHANGE_HOUR (3)
#define DEFAULT_PCO2_FAST_CHANGE_MINUTE (0)
#define DEFAULT_PCO2_FAST_CHANGE_SECOND (0)
#define DEFAULT_PCO2_FAST_LENGTH_YEAR (0)
#define DEFAULT_PCO2_FAST_LENGTH_MONTH (0)
#define DEFAULT_PCO2_FAST_LENGTH_DATE (0)
#define DEFAULT_PCO2_FAST_LENGTH_HOUR (0)
#define DEFAULT_PCO2_FAST_LENGTH_MINUTE (20)
#define DEFAULT_PCO2_FAST_LENGTH_SECOND (0)
#define DEFAULT_PCO2_RUN_LENGTH_YEAR (0)
#define DEFAULT_PCO2_RUN_LENGTH_MONTH (0)
#define DEFAULT_PCO2_RUN_LENGTH_DATE (0)
#define DEFAULT_PCO2_RUN_LENGTH_HOUR (20)
#define DEFAULT_PCO2_RUN_LENGTH_MINUTE (0)
#define DEFAULT_PCO2_RUN_LENGTH_SECOND (0)
#define DEFAULT_PCO2_O2_INTERVAL_YEAR (0)
#define DEFAULT_PCO2_O2_INTERVAL_MONTH (0)
#define DEFAULT_PCO2_O2_INTERVAL_DATE (1)
#define DEFAULT_PCO2_O2_INTERVAL_HOUR (0)
#define DEFAULT_PCO2_O2_INTERVAL_MINUTE (0)
#define DEFAULT_PCO2_O2_INTERVAL_SECOND (0)
#define DEFAULT_PCO2_O2_TIME_YEAR (0)
#define DEFAULT_PCO2_O2_TIME_MONTH (0)
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

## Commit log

2023-07-27 Adding flow control and pco2 to repo. Legal disclaimers added to README
2025-02-18 Update for new Kicad Schematics and Firmware
    [0ZCG0075FF2C.stp, 10118194-0001LF.step, 15v0_dc_regulator.kicad_sch, 15v_dc_regulator.kicad_sch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]
2025-02-18 Final update for new KiCAD files
    and proper opensource language
    [0ZCG0075FF2C.stp, 10118194-0001LF.step, 15v0_dc_regulator.kicad_sch, 15v_dc_regulator.kicad_sch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]
2025-02-18 add BOM and Schematic
    [BOM.xlsx]
2025-02-19 Add pco2sensor BOM and schematics
    [BOM.xlsx]
